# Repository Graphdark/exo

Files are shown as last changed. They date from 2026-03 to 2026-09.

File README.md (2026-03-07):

Это реабилитационный экзоскелет.

Полное руководство по сборке со всеми прошивками и моделями. К сожалению, я разрабатываю его для себя. Поэтому он точно работает. На моей странице ВК https://vk.ru/id7340591 есть видео его работы.

Начнём с того, что нам необходимо.
https://wokwi.com/projects/423680131662163969 симуляции проекта. Для работы я бы рекомендовал поставить плагин для VS Code или clion. Все необходимые файлы я положил.
Также для этих ide Необходим плагин PlatformIO
Для работы с моделями надо Компас 24

Прошить можно и Arduino IDE. Но я не знаю как.  
Теперь по комплектации.



Я очень дотошно и скрупулёзно забивал все названия. Поэтому просто берём название, копируем его, вставляем в поисковик.



Дальше просто поиск По картинкам. Не привожу ссылки на конкретные товары. Поскольку они очень быстро перестанут работать.
Обратите внимание, что доставка долгая с озона говорит то, что заказывают в Китае. Есть как минимум накрутка для Того, кто перепродаёт. Например, по аналогии ищем моторы.



Первая ссылка ведёт нас в Китай.



Срок доставки примерно такой же. При примерно такой же цене плюсом мы получим насадку. К тому же, эти моторы новее, но подойдут и с озона.

Для изготовления деталей нам нужна авито.



Всем троим скидываем на просчёт содержимое папки лазер. Спрашиваем сразу, чтобы окрасили. Выбираем самое дешёвое предложение. Режут быстро, получается красиво, точность нас устраивает.
Вообще можно делать из фанеры 5 или 7 миллиметров. Но все отверстия придётся делать самостоятельно. Идеально было бы Изготовить из алюминия или титана. Но это очень дорого. 
В моделях нет проводов. Но об этом я поговорю в инструкции.

По итогу У вас должна быть полная комплектация. Подробные инструкции есть в соответствующей папке.

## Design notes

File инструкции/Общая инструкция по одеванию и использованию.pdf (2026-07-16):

Общая инструкция по одеванию и использованию.

Весь экзоскелет состоит из шести частей:
- Две ноги;
- Пояс Для связи двух ног;
- Ортез;
- Ходунки с кнопками управления;
- Приборы;

Всё это разбирается.
То есть, вы одеваете сначала ортез.

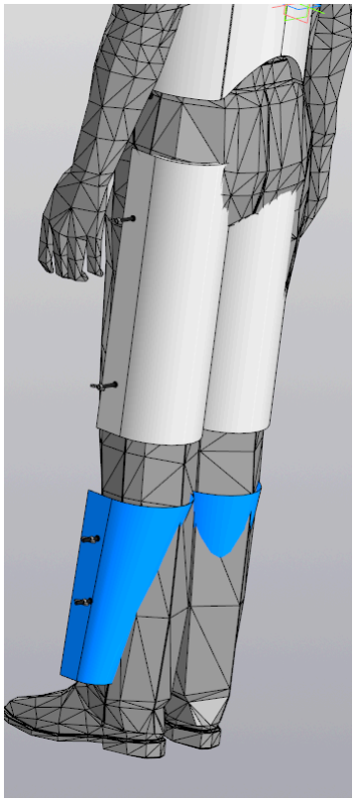
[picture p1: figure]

Ортез показан условно. Белым и синим цветом. Чёрные винты для крепления ног.
Крепите ноги.

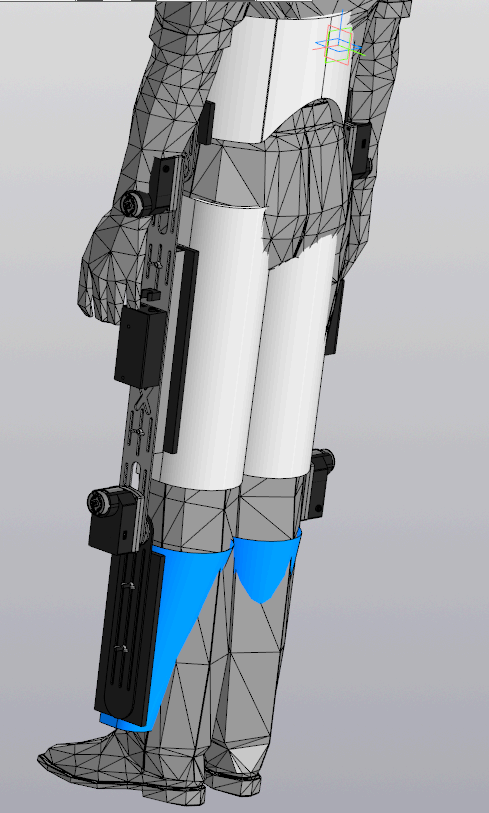
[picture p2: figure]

Связываете их поясом.

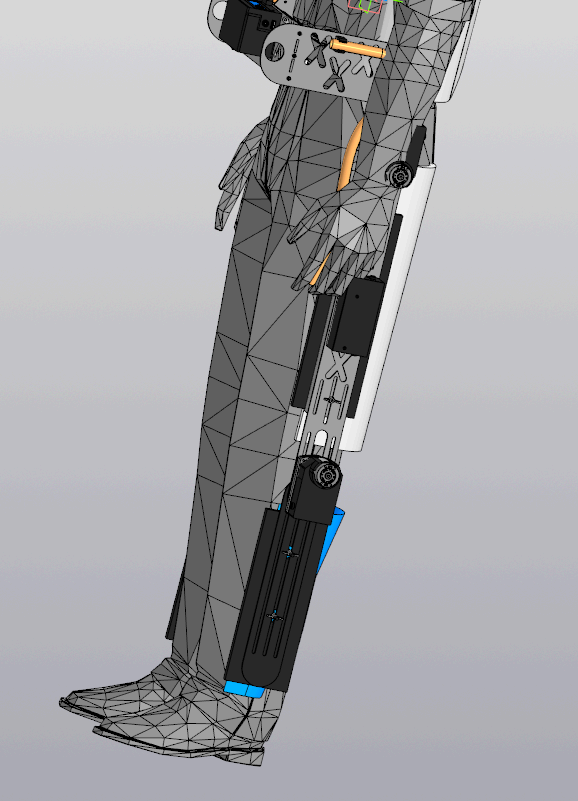
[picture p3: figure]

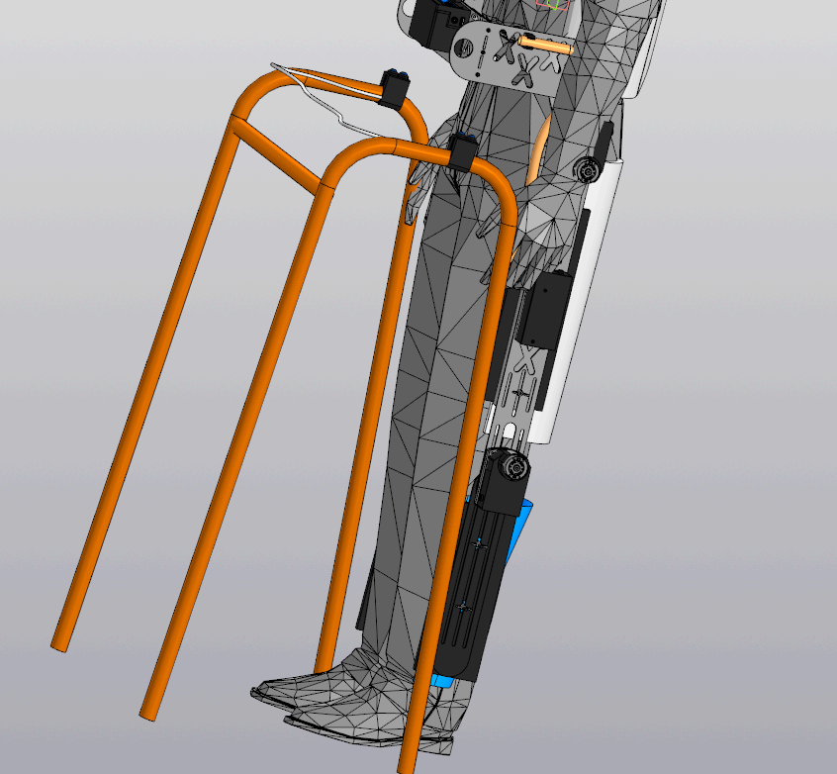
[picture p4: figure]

Подключаете ходунки.
Проверяйте все провода и можно пользоваться.

Небольшое дополнение по ходу испытаний. После прошивки новой версии программного обеспечения. Наблюдался очень интересный глюк. Два мотора на разных ногах начинали крутиться в другую сторону. Меня это было на моторах бедра. Причина этого неизвестно. Решается довольно просто.

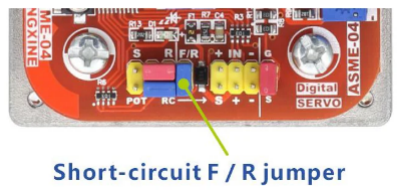
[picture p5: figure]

Нужно снять или поставить эту перемычку. Один раз было пришлось по новый угол настраивать.
Теперь самое важное. Все моторы завода настроены на максимальную скорость. Именно это мешает встать нормально. Это личные ощущение. Возможно, у вас все будет хорошо. Ну, можно снизить скорость вращения коленных моторов. Еще больше снизить скорость бращения бедренных моторов. Тогда из положения сидя. По команде встать. Туловище будет идти вперед, а колени разгибаться. При этом туловище будет подниматься, но медленнее. Возможно, так вставать будет легче. Скорость настраивается крутилкой, а.

При включении экзоскелет садится. Решение спорное. Я думаю, может, стоит оставить его стоя. Ну, пока так. Текущее состояние экзоскелета отображается на экране.

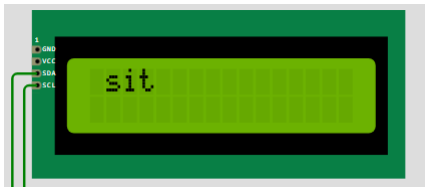
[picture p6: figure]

Следующая команда встать.

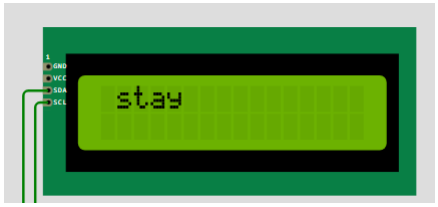
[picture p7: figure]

Происходит это резко. Для этого есть обоснование. Чтобы мозг не успел среагировать. Иначе мышцы может свести спастикой. В такой момент с ними не может работать даже взрослый и здоровый мужчина. Имею в виду Согнуть или разогнуть ногу. Относительно хилые моторы могут выйти из строя. У меня спастика бешеная. Я искал способы, как с ней бороться. Если вам это не нужно, я подскажу, как замедлить работу. Благо, исходники все есть.
Техника вставания. Стопы надо во что-то упереть. Руками надо опереться на ходунки. Лучше, чтобы сзади вас кто-то страховал. Вас держат за подмышки. При активации команды. Помогающий человек должен толкать вас вверх и вперед. Ноги полностью выпрямятся. Опирайтесь на них и на руки. Все это можно сделать и одному. Зависит от степени беспомощности. В любом случае я бы советовал потренироваться. При этом совсем не нужно одевать скелет на себя. Просто посадите его на стул. Упереть стопами в стену. Придерживая его, нажать команду, Встать. Следующая команда – это ходьба.

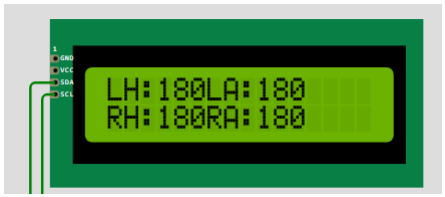
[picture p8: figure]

Цифрами показаны углы каждого привода. Left hip, right hip, left ankle, right ankle. Нажимаем кнопку левой или правой ноги, чтобы совершить шаг.

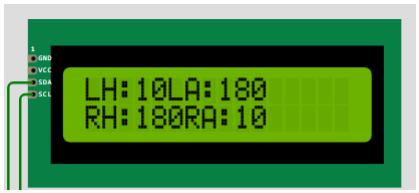
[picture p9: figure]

Поднимаем левое бедро на 10 градусов. Левое колено оставляем прямым. Опираемся на правое бедро. Отталкиваемся правым коленом на Десять градусов назад. Нажимаем другую кнопку, чтобы совершить шаг другой ногой.

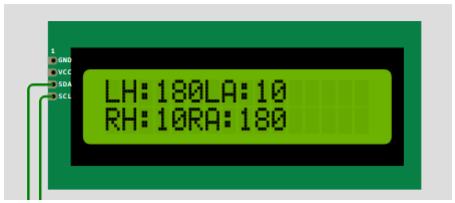
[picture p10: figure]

Замечу, что 10 градусов – это шаг здорового человека. В текущем коде я сильно сократил эти значения.
Подробнее посмотрим на метод ходьбы.

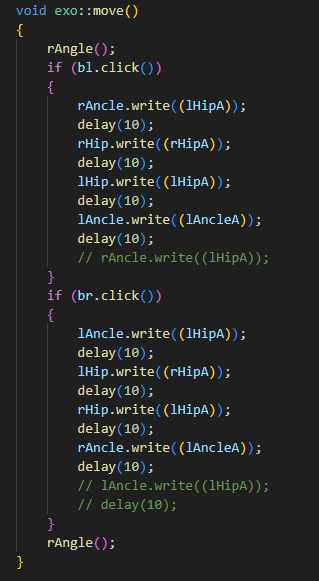
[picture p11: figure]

Я старался Избегать волшебных чисел. Поэтому я использовал переменные. Которые при объявлении инициализировал числом. Позже я покажу, как настраивать эти переменные. Соответственно, метод ходьбы может использоваться для того, чтобы хоть плясать.
Следующее у нас это шаги на месте.

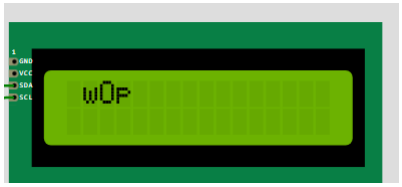
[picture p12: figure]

Walk on place. Простите мне мой английский. Принцип такой же, как с простой ходьбой, только на месте.
Переходим к настройкам.

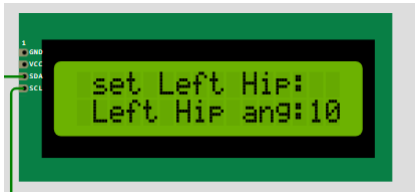
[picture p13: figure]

На экране написано, что мы меняем угол левого бедра. Кнопками левой и правой ноги можно менять значение. При этом действует диапазон, который надо менять в коде. Я его сделал для того, чтобы случайно не забить угол, который сломает ногу. Хотя эти моторы могут доставить только лёгкий дискомфорт. Но всё равно я решил себя обезопасить. По аналогии настраиваются все остальные углы. Выздоравливайте, пожалуйста.

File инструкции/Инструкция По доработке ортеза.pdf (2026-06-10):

Инструкция по Доработке Ортеза

На мой взгляд, это необязательная инструкция. Ну, всё-таки, на всякий случай, я её сделал. Из практики нашел очень интересный выход. Все это дорогое медицинское изделие из Китая не нужно. Само по себе оно дешевое. Стоит примерно как один мотор. Ну, бесплатной доставки нет. Поэтому я искал способ вообще избавиться от него. Ну, практика предложила гораздо более интересный и альтернативный вариант. Нам нужен пояс. Нам нужны две голени. Все это можно купить по отдельности. Для всего для этого можно искать бесплатную доставку. У меня нет нормальной модели ортеза. Поэтому выходит довольно криво. Но главное понять можно. Важное замечание, ничего сверлить в ортезе не надо. Все металлические детали имеют пазы по центру, как раз для крепления. Сам ортез имеет целую гору отверстий, по центральной части, как раз более толстой.

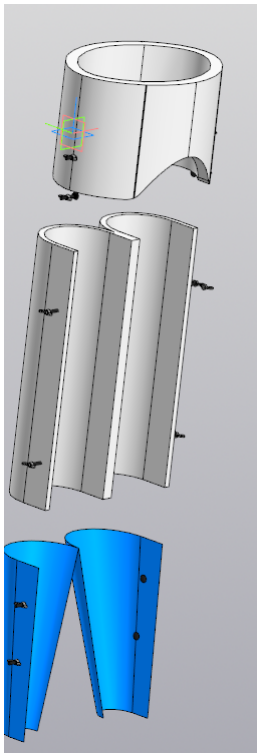
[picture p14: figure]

Удобней Это делать, когда ортез полностью на ноге. Комплектные металлические ограничители Надо снять. Это стальные полоски напротив сустава. Полностью собранную ногу переведите в положение сидя. Разметьте положение болтов согласно ноги.

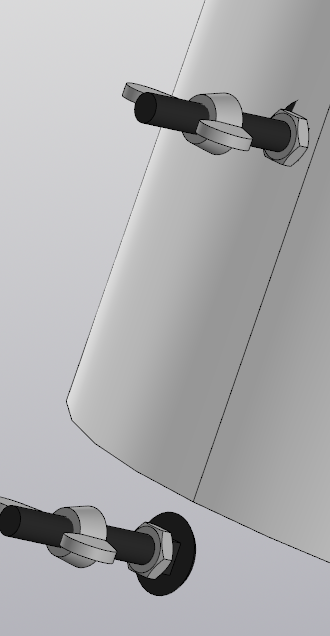
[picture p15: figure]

У меня один болт промахнулся, потому что модель Не точная. У вас такого быть не должно. Но здесь хорошо видно, что мы сначала вставляем болт и крепим гайкой. Барашки пока можно просто не ставить.

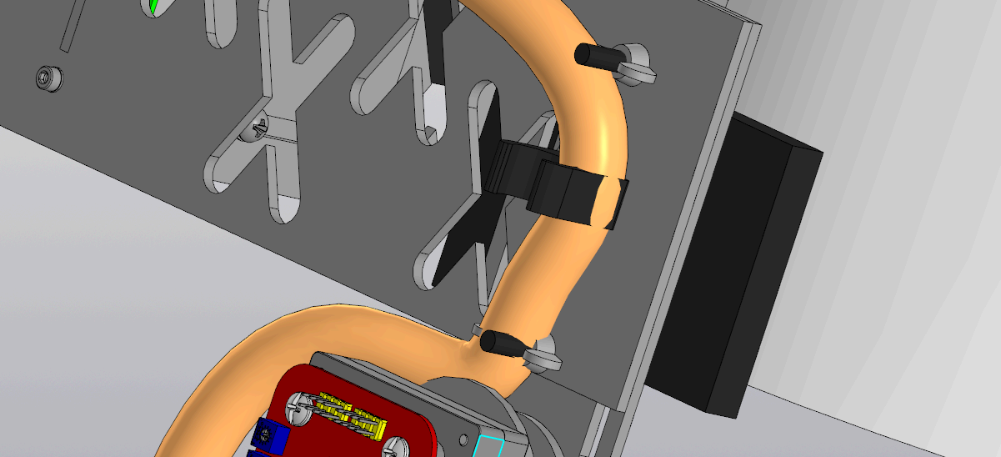
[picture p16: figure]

Они нужны для того, чтобы быстро прикрепить ногу и пояс. Ну и понятно, зачем мы сделали отверстие в прокладке(Под гайку).

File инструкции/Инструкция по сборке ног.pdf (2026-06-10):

Инструкция по сборке ног.

Итак, мы переходим к главному и последнему. Хотя, вообще-то, нет. Ещё напишу инструкцию на ходунки. Ну, даже поэтому можно оценить, что всё действительно просто. Вся цена это инженерная работа, программистская работа. Именно железо и комплектующие-Дешёвые. Самая дорогая часть — это моторы. Но китайские братья сильно Удешевили это. По большому счёту они не сделали ничего нового. Моторы, которые я разработал, гораздо более конструктивные. Они гораздо мощнее, но поскольку сам собрать я не могу, они пока на паузе. То есть я сделал один мотор, потягал им гирю и положил на полку. Хочу похвастаться, это действительно нестандартное решение. Но я отвлёкся, вернусь к теме нашей статьи.

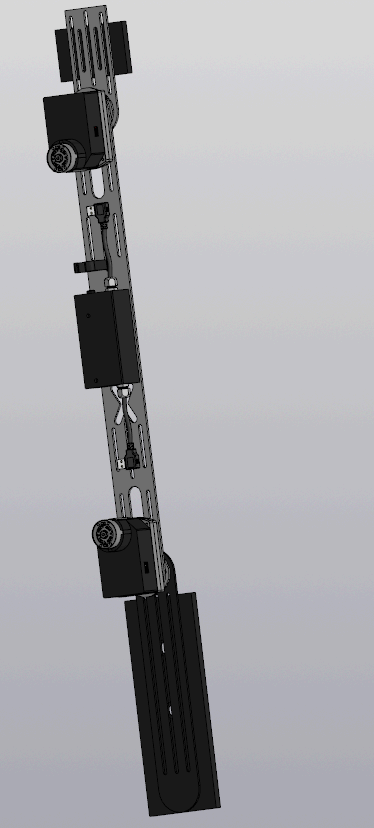
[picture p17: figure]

Прокладки не должны касаться насадки. Я бы рекомендовал приклеить их на двухкомпонентый клей. Нога не касается бедра. Прокладки выполняют декоративную функцию. Как показала практика, прокладки вообще не обязательны. В целом они не мешают, Поэтому я оставил их.
Прокладки делайте из поролона. Перед выполнением Отверстий проверьте по росту. Нам необходимо примерно подогнать. Эти пазы для точной подгонки. Итак, мы приклеили и выполнили отверстия. Крепим моторы.

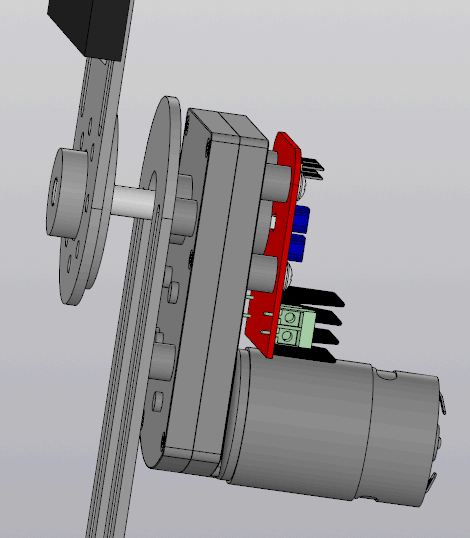
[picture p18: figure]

Обратите внимание на расположение насадки. Поставили два мотора, теперь делаем проводку. Опять же замечание из практики. Фиксировать мотор на насадке придется установочным винтом. Их продают на Озоне.

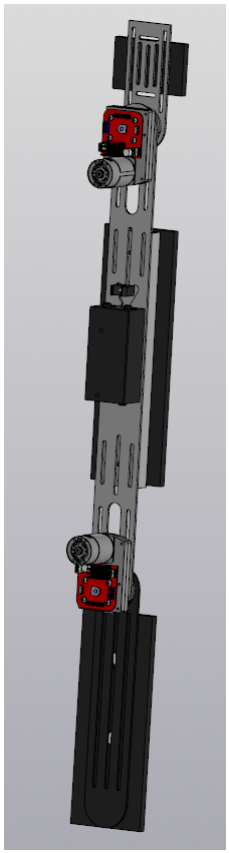
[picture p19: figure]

Клеем крепить клипсу. Блок-ноги крепить винтами.

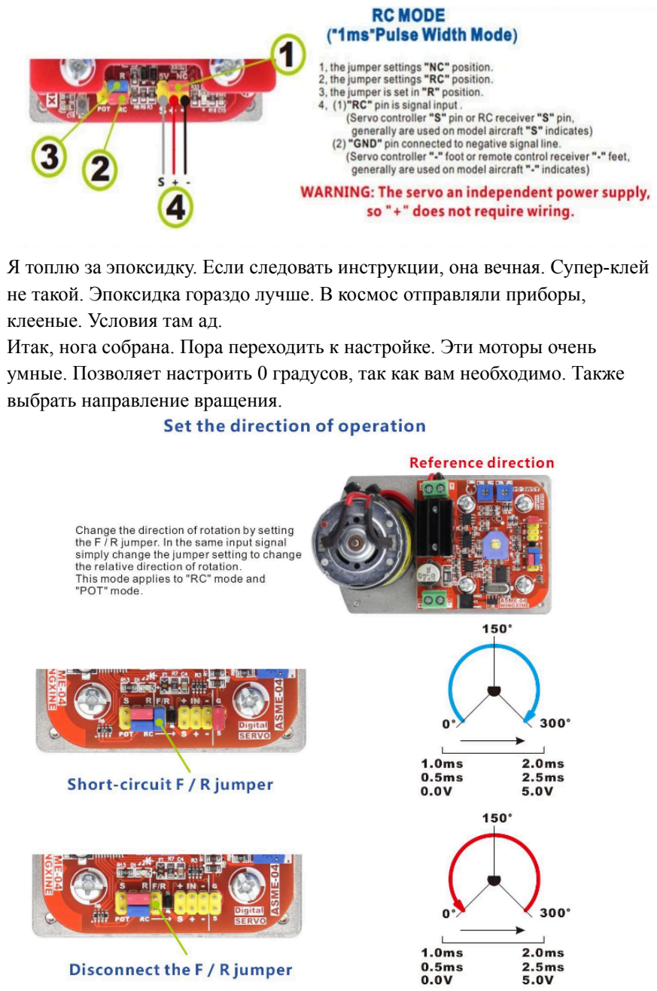
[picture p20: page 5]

Я топлю за эпоксидку. Если следовать инструкции, она вечная. Супер-клей не такой. Эпоксидка гораздо лучше. В космос отправляли приборы, клееные. Условия там ад.
Итак, нога собрана. Пора переходить к настройке. Эти моторы очень умные. Позволяет настроить 0 градусов, так как вам необходимо. Также выбрать направление вращения.

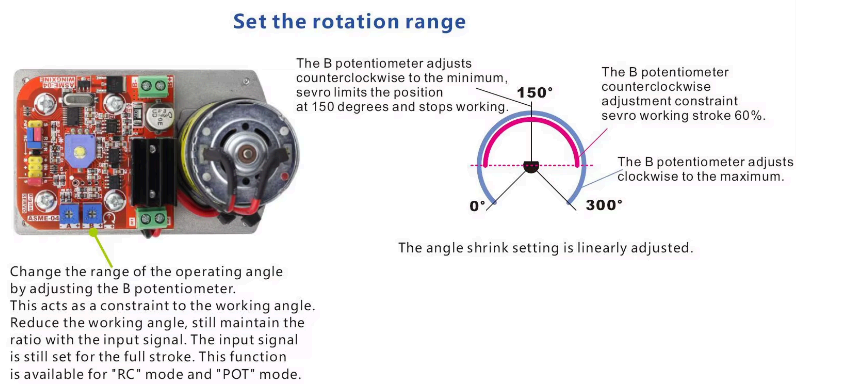
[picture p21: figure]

При включении Arduino командует вам сесть. Значит, торс прямо, бедро 90 градусов к торсу, колено 90 градусов к бедру. Именно так вам надо настроить ногу. Если у вас всё получилось, повторите это для другой ноги.

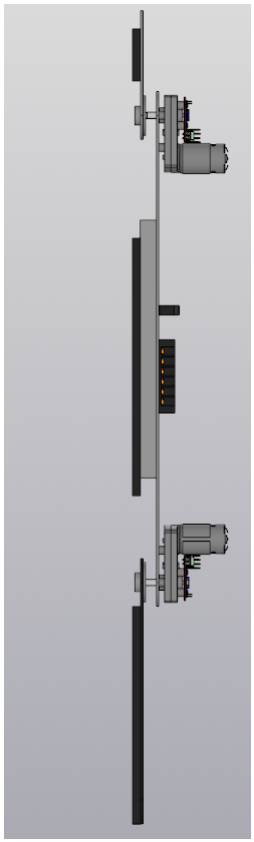
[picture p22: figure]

Поролоновые прокладки можно крепить прямо на ортез. То есть не ставить их на этапе этой сборки. Как удобнее, как правильнее, покажет только практика. К сожалению, мой удел только теория.

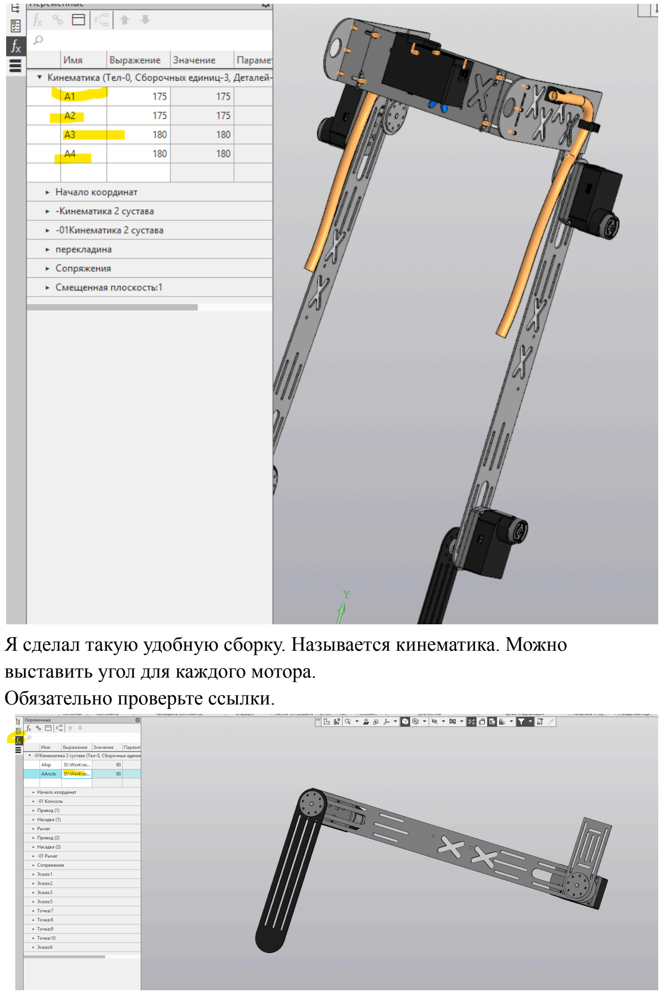
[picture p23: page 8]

Я сделал такую удобную сборку. Называется кинематика. Можно выставить угол для каждого мотора.
Обязательно проверьте ссылки.

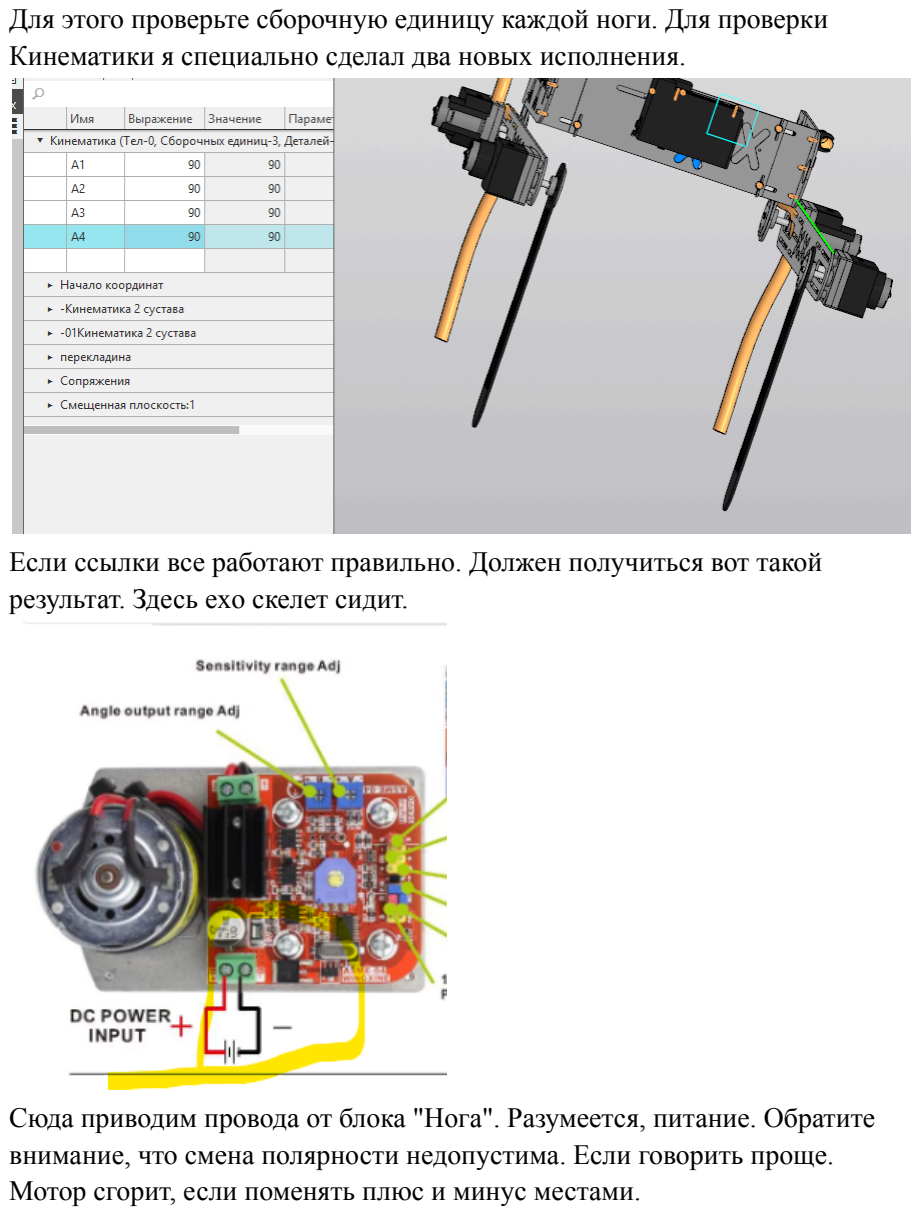
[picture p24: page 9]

Для этого проверьте сборочную единицу каждой ноги. Для проверки Кинематики я специально сделал два новых исполнения.

Если ссылки все работают правильно. Должен получиться вот такой результат. Здесь exo скелет сидит.

Сюда приводим провода от блока "Нога". Разумеется, питание. Обратите внимание, что смена полярности недопустима. Если говорить проще. Мотор сгорит, если поменять плюс и минус местами.


На всех четырех приводах. Вот так выставляем перемычки. С. Это управляющий сигнал. Плюс игнорируем. Минус — Это общий сигнал.

Два привода стоят на одной детали. Один привод будет вращаться по часовой стрелке, другой против.

Относительно такого положения мотора. Правое бедро по часовой стрелке. Колено против часовой стрелки. Настройка привода левой ноги зеркально.


Управление этим приводом точно такое же, как у любого другого. Минимальное напряжение — Это ноль градусов. Пять вольт — Это сто восемьдесят градусов. Удобнее, используя положение стоя. Ноль градусов. Смотрит вверх. Сто восемьдесят градусов. Смотрит вертикально вниз. Соответственно девяносто градусов — Это горизонтально. На картинке продавца диапазон триста градусов. Значит, что вы в нем можете расположить свои сто восемьдесят. Другими словами . Красную дугу. Можно расположить где угодно в пределах синей дуги.

Уже после меня пришла такая идея. Приводом можно управлять при помощи потенциометра. На странице товара даже есть в продаже. В магазине "Радио-товаров" Стоит рублей двадцать.


В этом магазине можно просто показать вот эту картинку.

Перемычки надо поставить, как на картинке. Как на картинке надо подключить потенциометр.

Крайнее левое положение резистора — Это ноль. Крайнее правое — Это сто восемьдесят. Дальнейшая настройка — Это очевидный процесс. На мой взгляд, очень удобно.

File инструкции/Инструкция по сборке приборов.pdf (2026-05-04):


Инструкция по сборке приборов.

Как по мне использование этих приборов повысило уровень моего скелета сильно. Их всего три. Два одинаковых прибора на ноги. И один вычислительный узел. Начнем с вычислительного узла.

Корпус я печатал на 3d-принтере. Это дешево, быстро и красиво.

Как выглядит прибор со снятой крышкой. Каждая плата встанет только на свое место. Все, что необходимо сделать, просто соединить проводками платы между собой.


Огромное преимущество использования компаса. То, что я могу выделить отдельный проводник. На самом деле только питание ардуины вызывает вопрос. Я использую преобразователь напряжения, чтобы снизить с двадцати четырех вольт до девяти. Есть в Озоне стоит рублей триста. Платы разъемов USb. Как и разъемы питания. Я бы рекомендовал покупать на aliexpress. Наши делают огромную наценку.

Прибор, блок-ноги — Это не совсем прибор. Это просто клемник, спрятанный в корпусе.


Просто паяем провода на соединители. После крепим их на клемник. Все очень просто. Корпус И кабельные вводы тоже печатаны на 3d-принтере. Схема монтажа, в папке инструкции.

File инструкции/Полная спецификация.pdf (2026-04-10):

Полная спецификация.

Рекомендательный документ. Делаю его больше для себя. Пойду прямо по отдельным сборкам.
- Ortonica XS 305 Ходунки
- Выключатель-кнопка без фиксации Четыре штуки.
- Две печатные детали.
- Два usb провода.
- Один хороший usb удлинитель.
Пока собираем ходунки, режьте металл. Режут его быстро, но ходунки собирать тоже быстро.
- Шайба м3, шесть штук.
- Гайка м3, шесть штук.
- Винт м3х10, шесть штук.
- 8 винта или болта м5х16.
- Четыре стопорные шайбы, М5.
- 16 простых шайб м5.
- Четыре гайки, м5.
- Четыре гайки-барашки м5.
- Аккумулятор 24 В 6s2p 40000 мАч.
- Держатель с фиксатором для труб D16мм черный 4шт.
- Гофра для кабеля 16 мм, один метр.
Прибор ЦПУ. Пока для него едет все то, что заказали. Распечатайте корпус.
- Ардуина Нано.
- LCD_1602_I2C
- LM2596 DC-DC stepdown voltage converter
- кронштейн Печатная деталь.
- Nano адаптер v1.0 Shield для ардуино с винтовыми зажимами
- винт м2х13 2шт.
- Шайба м2 4 штуки.
- Гайк, м2 2 штуки.
- USB2.0 «мама» на 4P DIP 3шт.
- Крышка Печатная деталь.
Нога. Ноги у нас две учитывайте. Весь крепеж и насадки для мотора должны быть в комплекте с мотором. Если вы покупаете насадки отдельно, берите те, у которых нарезана резьба. Есть отверстие для стопорения на валу. Для стопорения комплектный винт упрется шляпкой. Нужно купить четыре установочных мента того же диаметра. Это винты без шляпки. Их легко можно изготовить самому.
- Труба прямоугольная алюминий 40x20x1.5 1м
- Вторичный поролон RBD 140 лист 10x1000x2000мм
- Держатель с фиксатором для труб D16мм черный 2шт
Корпус прибора ноги Печатается на принтере.
- ТВ 2506 клеммник 2шт.
- DC разъём питания 5,5х2,1/5,5х2,5 мм чёрный На две ноги их надо шесть штук. Всего их надо 13.
- USB2.0 «мама» на 4P DIP На ноги их надо шесть. Всего их надо 13.
- болт с полукруглой головкой 5x30 4 шт
- Гайка, м5 4шт.
Привода. Корпуса для них печатаем на принтере.
- ASME -04B Servo 380кгс/см 4шт
- USB2.0 «мама» на 4P DIP 4шт
- DC разъём питания 5,5х2,1/5,5х2,5 мм чёрный 4шт
Сборка верхнего уровня. Когда собрано уже все, надо только собрать все вместе.
- Гайка м5 12 штук. Всего их надо шестнадцать.
- Гайки, барашки, м5 12шт. Всего их надо шестнадцать.
- болт с полукруглой головкой 5x30 12 шт Всего их надо шестнадцать.
- Реабилитация ног, поясной бандаж, поддержка колена, регулируемый ортез для натяжения связок, ортез для реабилитации мениска, корректор лодыжки
- Удлинительный кабель 12В 5,5х2,5 мм Конкретно их полуметровых надо два. Нужны еще восемь коротких. От приводов до прибора ног.
- USB 3.0 удлинитель кабель Два полуметровых. Восемь каратышей.
- FiJila 24В 40000 мАч литиевый аккумулятор
На этом все вроде бы ничего не забыл.

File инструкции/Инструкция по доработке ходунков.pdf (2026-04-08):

Инструкция По доработке ходунков

Многое в этой инструкции просто рекомендательный характер. Призываю ничего не крепить жёстко. Тогда это управление вы сможете использовать на разных ходунках.


Провод у самих клипс, только прикрепите стежками. Чтобы не оторвались в случае падения ходунков. Остальное можно крепить просто изолентой. Провода, как и раньше, я использую USB.


Две такие детали надо распечатать. Они спроектированы под те кнопки, что сейчас установлены в модели. Комплектные гайки просто ставим снизу. Сверху вкручиваем сами кнопки.
У двух кнопок одна общая земля. Два управляющих провода. То есть из USB кабеля вы будете использовать только три провода. Делаем две такие клипсы под каждую руку.


Провода сводим примерно таким образом. Естественно, что В воздухе у вас ничего не висит. Провода крепим к Ходункам. Сводим вместе и паяем земли от обеих рук. Всего у вас задействовано 5 проводов. Четыре провода, управляющие от кнопок, и одна земля. Теперь вам нужен На растерзание USB удлинитель. Отрезаем от него мама-часть. Очищаем провода. В нём четыре сигнальных и оплётка земли. Четыре сигнальных провода используем для управления кнопками. Оплётку Земли соединяем с общим. Когда мы собирали Прибор ЦПУ, там был лишний USB.


Я думаю, понятно, зачем этот кабель.


С одной стороны мы подключаем его к Arduino. С другой подключаем Наши ходунки с кнопками. Не забудьте прозвонить сигналы от кнопок до Ардуино. Место стыковки кабелей лучше закрыть термоусадочной трубкой. Наша задача была сделать кабеля с кнопками на концах.

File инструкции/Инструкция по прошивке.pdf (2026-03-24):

Инструкция по прошивке

В интернете полно информации. Но всё же вот.

Работать будем вот с этим каталогом. Устанавливаем VS Code, запускаем.


В расширениях ищем PlatformIO, устанавливаем. Запускаем его.


У меня он ставился долго. Появление домика в левом нижнем углу говорит о том, что он установился.


Открываем наш проект.


Собственно, это всё.

Жмём «Компилировать»

Вот такую картинку мы должны получить.

Вообще, для этой инструкции я делаю буквально всё, что показываю. Поэтому у вас обязательно должна получиться именно такая картинка.


После просто жмём прошить. Arduino у вас уже подключено. То есть, провод USB В ней уже стоит. Прошивается довольно быстро.

Совсем необязательно, но можно установить симулятор прямо в визуал студию.

Находим И устанавливаем это дополнение.

После открываем файл. Возможно, у вас запросит бесплатный ключ. Ну там всё просто. Пусть не спущает то, что у меня здесь стоит Ардуина Уна. С нано различий нет никаких. Лично я этот симулятор использовал для отладки, очень удобно.


Я обнял схему на новую. От Старой отличается только внешне.

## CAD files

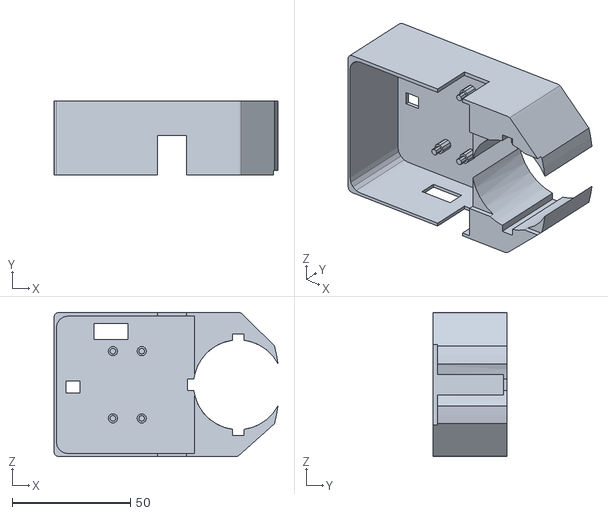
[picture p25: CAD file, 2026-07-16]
3d Печать/Корпус.stl
94.8 x 31.5 x 61.0

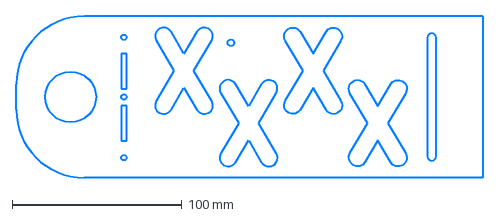
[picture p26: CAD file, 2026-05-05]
лазер/3мм-2шт.dxf
275.0 x 95.0 mm

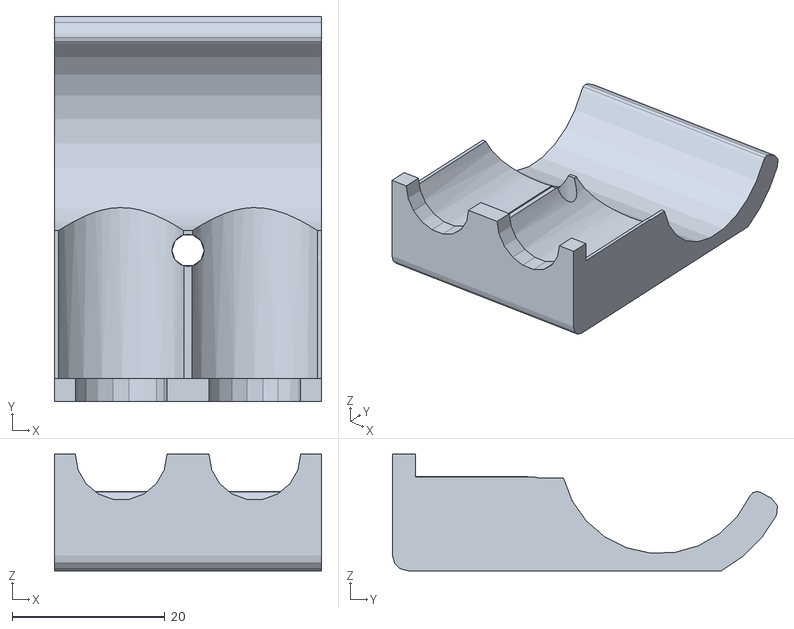
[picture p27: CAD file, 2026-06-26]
3d Печать/Крепеж 25 мм.stl
35.0 x 50.4 x 15.2

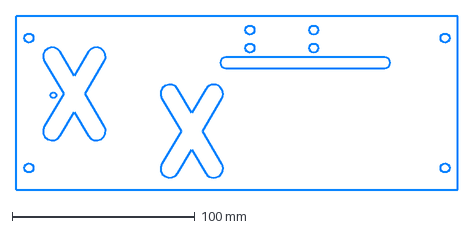
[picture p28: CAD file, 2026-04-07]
лазер/3мм-1шт.dxf
241.8 x 95.0 mm

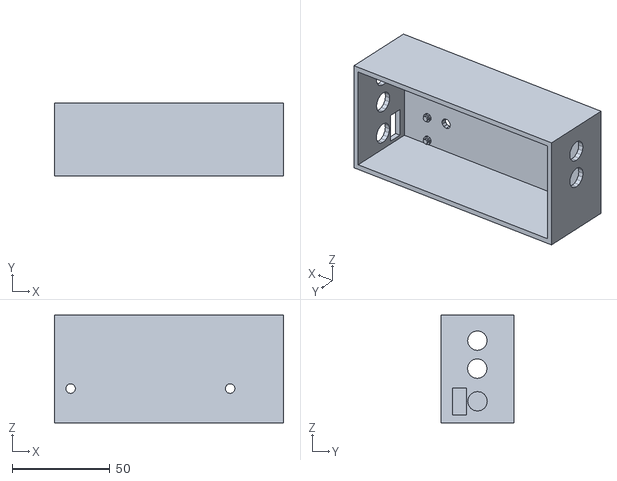
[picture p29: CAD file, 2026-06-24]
3d Печать/Корпус Нога.stl
117.0 x 37.5 x 55.0

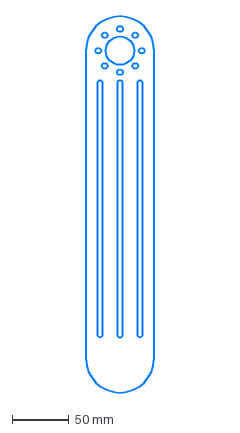
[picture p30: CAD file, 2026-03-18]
лазер/3мм -4шт.dxf
60.0 x 330.0 mm

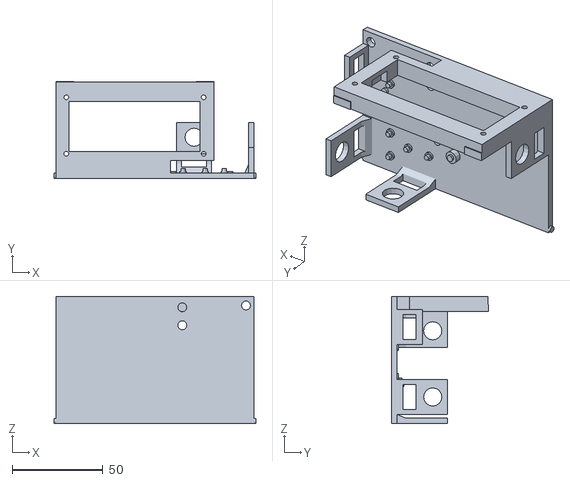
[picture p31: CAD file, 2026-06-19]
3d Печать/кронштейн ЦПУ.stl
111.0 x 53.5 x 70.0

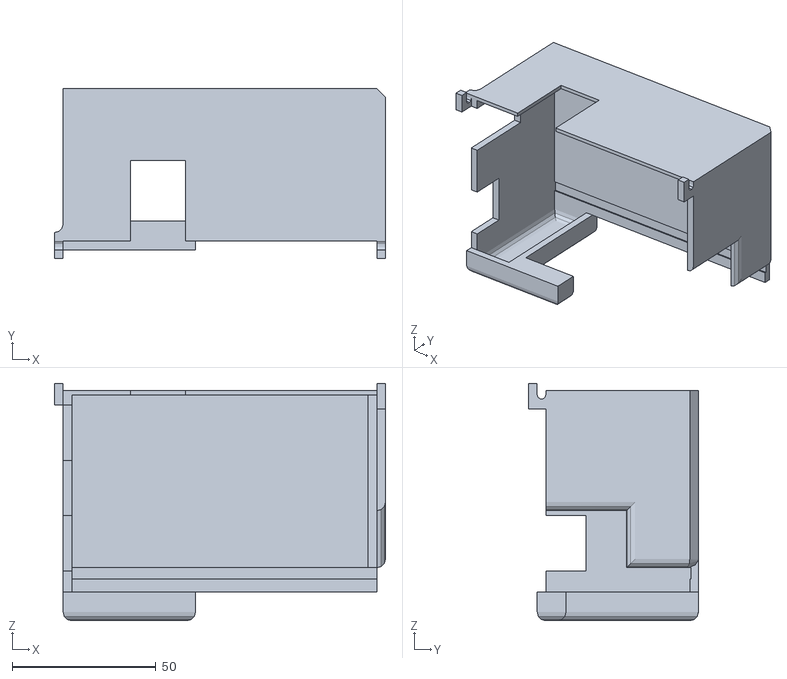
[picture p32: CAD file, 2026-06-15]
3d Печать/Крышка ЦПУ.stl
115.0 x 59.0 x 82.5

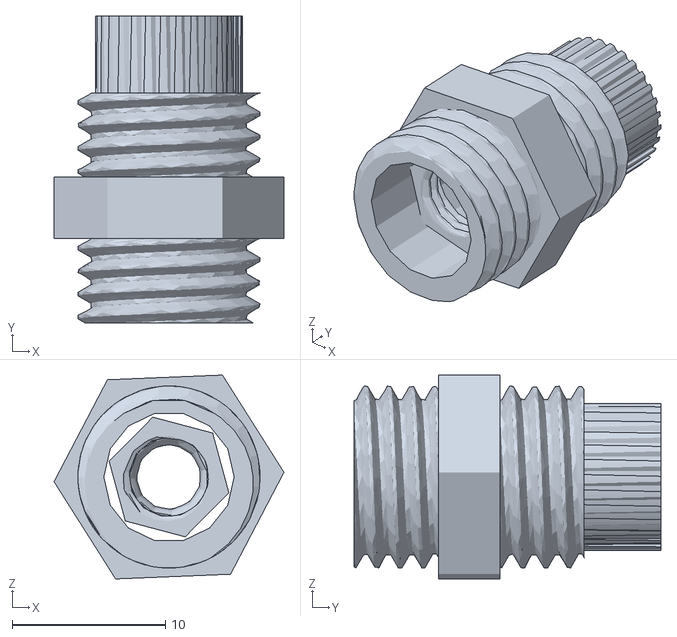
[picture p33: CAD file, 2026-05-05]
3d Печать/Кабельный ввод.1.stl
15.0 x 20.0 x 13.3

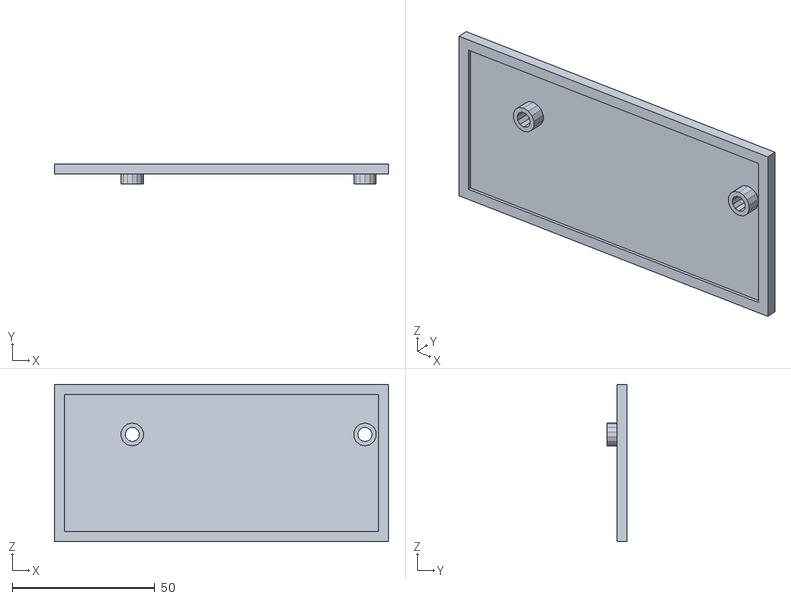
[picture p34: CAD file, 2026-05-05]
3d Печать/Крышка нога.stl
117.0 x 7.00 x 55.0

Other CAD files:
лазер/3мм -2шт.dxf
лазер/3мм -2шт.dxf

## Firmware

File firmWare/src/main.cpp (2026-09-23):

#include "exo.h"
#include "GBUS.h"
#include <SoftwareSerial.h>

#define GBUS_PIN 2
#define GBUS_BAUD 9600

SoftwareSerial gbusSerial(GBUS_PIN, 20);
GBUS slave(&gbusSerial, 2, 64);

struct ServoCommand {
  uint8_t lh, lk, rh, rk;
  uint8_t btn;
  uint8_t interval;
};

ServoCommand cmd;
int prev_lcmd = -1; // -1 гарантирует, что первая команда выведется при старте

const int lHip = 10;
const int lAncle = 9;
const int rHip = 8;
const int rAncle = 7;

const int UpB = 6;
const int bD = 5;
const int leftb = 11;
const int rightb = 12;

// LiquidCrystal_I2C lcd(0x27, 16, 2);
bool needPrint = false;
exo fexo;
button butD, bup;
int lcmd = 0;

bool handleGBUS() {
  ServoCommand cmd;
  if (slave.readData(cmd)) {          // шаблонный readData, 1 аргумент
    if (cmd.btn == 3) { fexo.smoothStand(); return; }
    if (cmd.btn == 4) { fexo.smoothSit();   return; }
    // if (cmd.btn == 1) localBtnLTrigger = cmd.lh;
    // if (cmd.btn == 2) localBtnRTrigger = cmd.rh;
    // fexo.servRul(cmd.lh,cmd.lk,cmd.rh,cmd.rk);
    return true;
  }
}

void setup()
{
  Serial.begin(9600);
  pinMode (LED_BUILTIN, OUTPUT);
  fexo.atach(lHip,lAncle,rHip,rAncle,leftb,rightb);
  fexo.smoothSit();
  butD.atach(bD);
  bup.atach(UpB);
  gbusSerial.begin(GBUS_BAUD);

  fexo.lcdPrint("load");
  delay(2000);
}

void loop()
{
  // lcd.clear();
  slave.tick();

  if (butD.click())
  {
    if (lcmd != 0) lcmd = lcmd-1;
  }
  if (bup.click())
  {
    if (lcmd != 3) lcmd = lcmd+1;
  }

  if (lcmd != prev_lcmd) {
        fexo.lcdPrint(fexo.fcmd[lcmd]);       // Вывод на LCD (только при изменении)
        Serial.println(fexo.fcmd[lcmd]);      // Вывод в Serial с новой строкой
        
        prev_lcmd = lcmd;                     // Запоминаем новое состояние как "предыдущее"
    }
  // if (fexo.bl.click())  //Если нажата левая лампочка горит.
  // {
  //   digitalWrite(LED_BUILTIN,HIGH);
  // }
  //   if (fexo.br.click())//Если нажата правая лампочка гаснет.
  // {
  //   digitalWrite(LED_BUILTIN,LOW);
  // }
  
  switch (lcmd)
  {
    case 0:
    {
      fexo.sit();
      break;
    }
    case 1:
    {
      fexo.stay();
      break;
    }
    case 2:
    {
      fexo.move();
      break;
    }
    case 3:
    {
      fexo.wOtS();
      break;
    }
  }

  if (handleGBUS())
  {
    fexo.servRul(cmd.lh,cmd.lk,cmd.rh,cmd.rk);
  }
  delay(10);
}

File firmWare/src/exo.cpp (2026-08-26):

#include "exo.h"

void exo::setLegPos(bool l, int p) {
    switch (p) {
        case 0: // Сидя
            smoothSit(); // Плавное садение
            break;
            
        case 1: // Стоя
            smoothStand(); // Плавное вставание
            break;
            
        case 2: // Шаг
            if (l) {
                rHip.write(stayA); rAncle.write(stayA);
                lHip.write(lHipA); lAncle.write(stayA-lHipA);
            } else {
                lHip.write(stayA); lAncle.write(stayA);
                rHip.write(rHipA); rAncle.write(stayA-rHipA);
            }
            break;
            
        case 3: // Шаг на месте
            if (l) {
                rHip.write(stayA); rAncle.write(stayA);
                lHip.write(sitHip); lAncle.write(sitAncle);
            } else {
                lHip.write(stayA); lAncle.write(stayA);
                rHip.write(sitHip); rAncle.write(sitAncle);
            }
            break;
            
        default:
            break;
    }
}

exo::exo()
{
}

void exo::atach(int Hipl, int Anclel, int Hipr, int Ancler, int butL, int butR)
{
    lHip.attach(Hipl);
    lAncle.attach(Anclel);
    rHip.attach(Hipr);
    rAncle.attach(Ancler);
    bl.atach(butL);
    br.atach(butR);
    lcd.attach(0x27, 16, 2);//0x20
    lcd.init();
    lcd.backlight();
}

void exo::servRul(int lH, int lA, int rH, int rA)
{
    lcdPrint("server");
    lHip.write(lH);
    lAncle.write(lA);
    rHip.write(rH);
    rAncle.write(rA);
}

void exo::lcdPrint(String str)
{
    int l = (16 - str.length())/2;
    lcd.clear();
    lcd.setCursor(l,0);
    lcd.print(str);
}

void exo::move()
{
    if (bl.click())
    {
        setLegPos(true,2);
    }
    if (br.click())
    {
        setLegPos(false,2);
    }
}

// void exo::setLHipA()
// {
//     if (bl.click() && lHipA < 180) lHipA++;      // +1 градус
//     else if (br.click() && lHipA > 0) lHipA--;   // -1 градус
//     lcdPrint("Left Hip ang:" + lHipA);
// }

// void exo::setLAncleA()
// {
//     if (bl.click())
//     {
//         if (lAncleA == 180) lAncleA = lAncleA;
//         lAncleA += lAncleA;
//     }
//     else if (br.click())
//     {
//         if (lAncleA == 30) lAncleA = lAncleA;;
//         lAncleA -= lAncleA;
//     }
//     lcdPrint("Left Anc ang:" + lAncleA);
// }

// void exo::setRHipA()
// {
//     if (bl.click())
//     {
//         if (rHipA == 135) rHipA = rHipA;
//         rHipA += rHipA;
//     }
//     else if (br.click())
//     {
//         if (rHipA == 0) rHipA = rHipA;
//         rHipA -= rHipA;
//     }
//     lcdPrint("RightHip ang:" + lHipA);
// }

// void exo::setRAncleA()
// {
//     if (bl.click())
//     {
//         if (rAncleA == 180) rAncleA = rAncleA;
//         rAncleA += rAncleA;
//     }
//     else if (br.click())
//     {
//         if (rAncleA == 30) rAncleA = rAncleA;
//         rAncleA -= rAncleA;
//     }
//     lcdPrint("RightAnc ang:" + rAncleA);
// }

String exo::rAngle()
{
    String res = String(lHip.read()) + " " + String(lAncle.read()) + " " + String(rHip.read()) + " " + String(rAncle.read());
    return res;
}

void exo::sit()
{
    setLegPos(true,0);
}

void exo::wOtS()
{
    if (bl.click())
    {
      setLegPos(true,3);
    }
    if (br.click())
    {
      setLegPos(false,3);
    }
}

void exo::stay()
{
    setLegPos(true,1);
}

void exo::smoothStand() {
    int currentLHip = lHip.read();
    int currentLAncle = lAncle.read();
    int currentRHip = rHip.read();
    int currentRAncle = rAncle.read();
    
    const int hipDelay = 60;    // Бедро: замедление на 75% (в 4 раза медленнее базовых 15мс)
    const int ancleDelay = 30;  // Колено: замедление вдвое (в 2 раза медленнее)
    
    unsigned long lastHipMove = 0;
    unsigned long lastAncleMove = 0;
    
    while (currentLHip != stayA || currentLAncle != stayA || 
           currentRHip != stayA || currentRAncle != stayA) {
        
        unsigned long now = millis();
        
        // Двигаем бедра (медленно)
        if (now - lastHipMove >= hipDelay) {
            if (currentLHip != stayA) {
                currentLHip += (stayA > currentLHip) ? 1 : -1;
                lHip.write(currentLHip);
            }
            if (currentRHip != stayA) {
                currentRHip += (stayA > currentRHip) ? 1 : -1;
                rHip.write(currentRHip);
            }
            lastHipMove = now;
        }
        
        // Двигаем колени (быстрее)
        if (now - lastHipMove >= ancleDelay) {
            if (currentLAncle != stayA) {
                currentLAncle += (stayA > currentLAncle) ? 1 : -1;
                lAncle.write(currentLAncle);
            }
            if (currentRAncle != stayA) {
                currentRAncle += (stayA > currentRAncle) ? 1 : -1;
                rAncle.write(currentRAncle);
            }
            lastAncleMove = now;
        }
    }
}

void exo::smoothSit() {
    int currentLHip = lHip.read();
    int currentLAncle = lAncle.read();
    int currentRHip = rHip.read();
    int currentRAncle = rAncle.read();
    
    const int hipDelay = 15;    // Бедро: быстро
    const int ancleDelay = 30;  // Колено: медленно (в 2 раза)
    
    unsigned long lastHipMove = 0;
    unsigned long lastAncleMove = 0;
    
    while (currentLHip != sitHip || currentLAncle != sitAncle || 
           currentRHip != sitHip || currentRAncle != sitAncle) {
        
        unsigned long now = millis();
        
        // Двигаем бедра (быстро)
        if (now - lastHipMove >= hipDelay) {
            if (currentLHip != sitHip) {
                currentLHip += (sitHip > currentLHip) ? 1 : -1;
                lHip.write(currentLHip);
            }
            if (currentRHip != sitHip) {
                currentRHip += (sitHip > currentRHip) ? 1 : -1;
                rHip.write(currentRHip);
            }
            lastHipMove = now;
        }
        
        // Двигаем колени (медленно)
        if (now - lastAncleMove >= ancleDelay) {
            if (currentLAncle != sitAncle) {
                currentLAncle += (sitAncle > currentLAncle) ? 1 : -1;
                lAncle.write(currentLAncle);
            }
            if (currentRAncle != sitAncle) {
                currentRAncle += (sitAncle > currentRAncle) ? 1 : -1;
                rAncle.write(currentRAncle);
            }
            lastAncleMove = now;
        }
    }
}

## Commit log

2026-03-09 Create Инструкция по сборке ноги.pdf
2026-03-09 Update Инструкция по сборке ноги.pdf
2026-05-03 Манекен
2026-05-04 Пока без него соберем.
2026-05-04 лазер
    [3мм -2шт.dxf, 3мм-2шт.dxf]
2026-05-12 Update Кабельный ввод.2.stl
    [Кабельный ввод.2.stl]
2026-05-25 Create Схема Привод.frw
